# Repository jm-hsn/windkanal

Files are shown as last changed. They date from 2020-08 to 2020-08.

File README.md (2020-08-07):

# Windkanal HSN

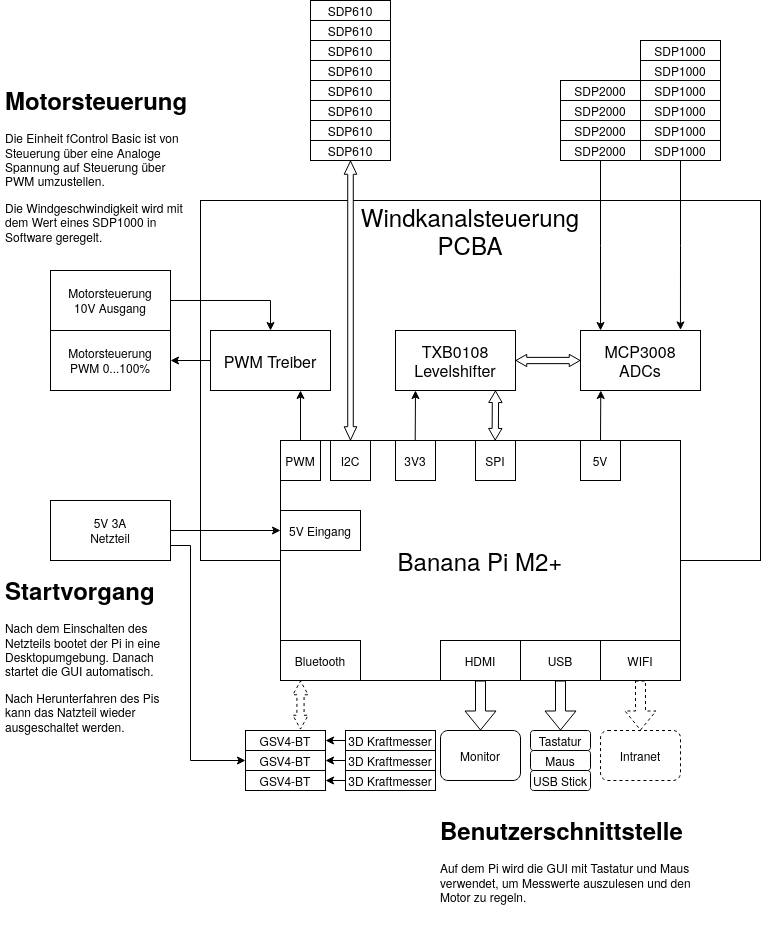
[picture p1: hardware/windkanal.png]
Hardware Chart


# Hardware
[PCB](https://easyeda.com/User201/windkanal)

[Gerber Dateien](hardware/pcb)

[Komponentenliste](hardware/bom.md)

## GPIO Pinout

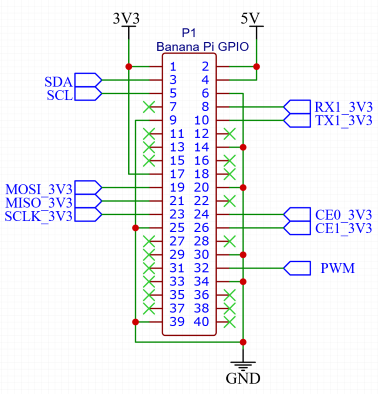
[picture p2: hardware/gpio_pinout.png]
GPIO Pinout


# Installation
[software/install.md](software/install.md)

# Starten

```bash
cd software/
python3 main.py
```

# Entwicklung
[software/ui/README.md](software/ui/README.md)

## Guides
PyQt5 Tutorial https://likegeeks.com/pyqt5-tutorial/

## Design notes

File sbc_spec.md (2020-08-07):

- bluetooth
  - serial over bt
  - bluetooth dongle?
- Raspberry Pi compatible GPIO
  - I2C
  - Parallel (bit-bang)

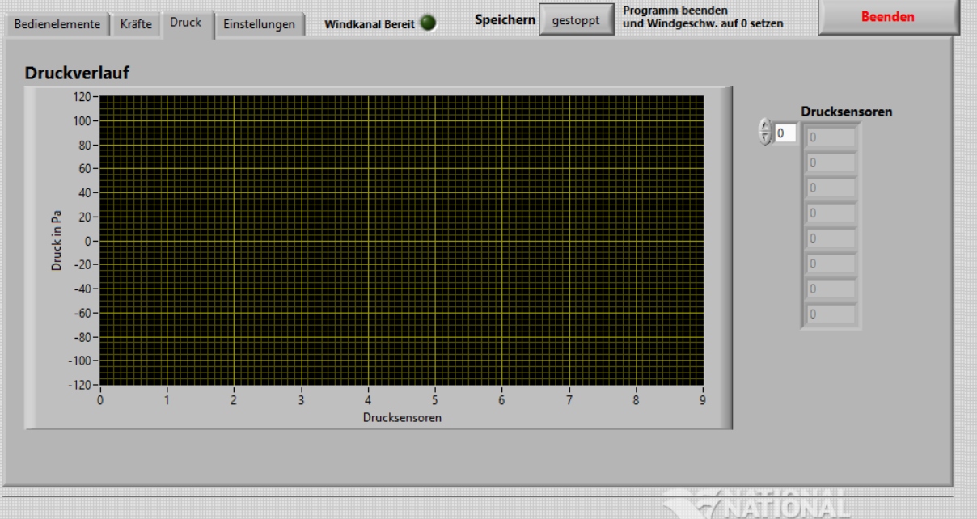
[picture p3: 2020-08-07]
software/labview/druck.jpg

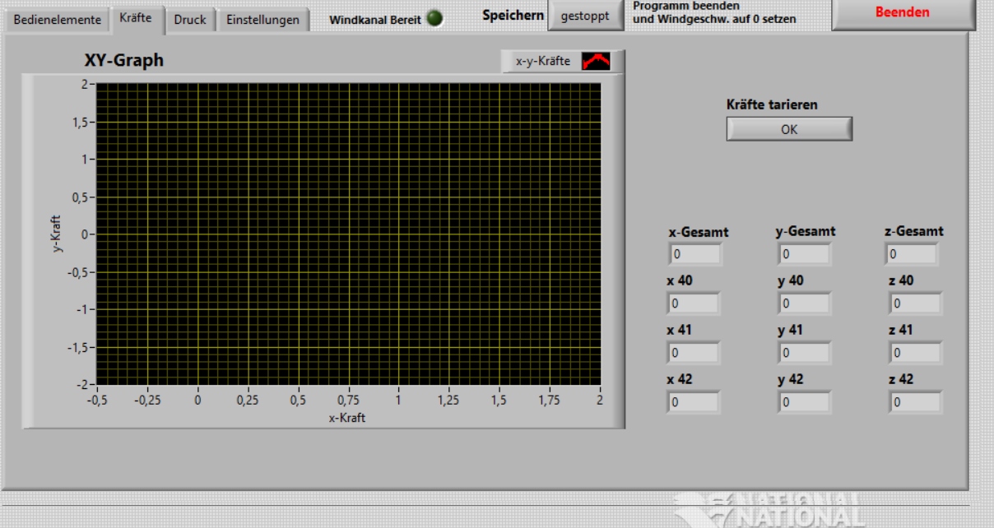
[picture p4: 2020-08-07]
software/labview/kräfte.jpg

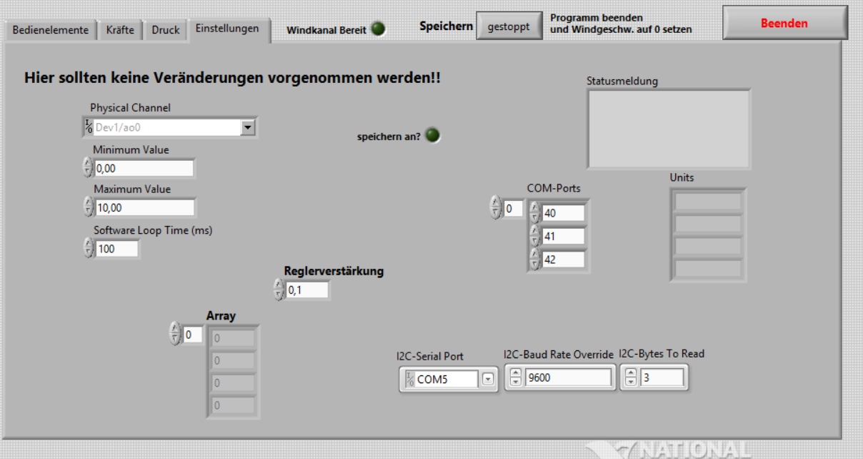
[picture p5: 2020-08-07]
software/labview/einstellungen.jpg

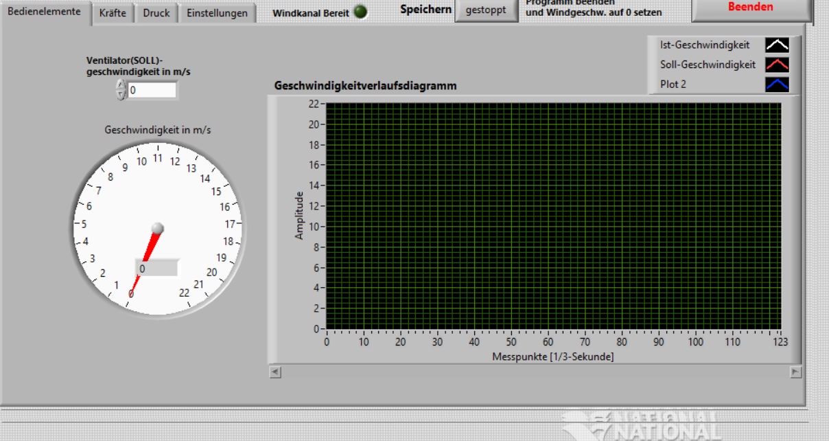
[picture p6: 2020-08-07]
software/labview/bedienelemente.jpg

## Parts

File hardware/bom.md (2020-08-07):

# Komponentenliste [BOM](hardware/pcb/bom.xlsx)

| Designator                                        | Name                         | Footprint    | Stück |
|---------------------------------------------------|------------------------------|--------------|-------|
| C1,C6,C2,C5                                       | SMD Kondensator              | 0805'        | 4     |
| R2,R3,R4,R5,R5,R7,R8                              | SMD Widerstand               | 0805'        | 7     |
| R1                                                | SMD Widerstand               | 0805'        | 1     |
| LED1                                              | Led Grün                     | 5mm          | 1     |
| LED2                                              | LED Rot                      | 5mm          | 1     |
| LED3                                              | LED Gelb                     | 5mm          | 1     |
| Q1,Q4                                             | SMD NPN Transistor           | SOT\-23      | 2     |
| Q2                                                | SMD PNP Transistor           | SOT\-23      | 1     |
| U2,U5                                             | 8\-Kanal SPI ADC             | SOIC\-16     | 2     |
| U4                                                | Bidirektionaler Pegelwandler | SSOP\-20     | 1     |
| JP1\-JP7                                          | Zweifach\-Schraubklemme      | 3,5mm pitch  | 15    |
| P1                                                | 2x20\-pin stackable Header   | 2,54mm pitch | 1     |
| H1                                                | 1x3\-pin stackable Header    | 2,54mm pitch | 1     |
| [PCB](https://easyeda.com/User201/windkanal) | 65mm x 65mm                  | \-           | 1     |
| Banana Pi BPI\-M2\+                               | Single\-Board\-Computer      | \-           | 1     |
| M2\.5 Abstandshalter für PI und PCB               | M2\.5, 10mm                  | \-           | 4     |
| Netzteil                                          | 5V 3A                        | \-           | 1     |
| HDMI Verlängerungskabel zum Einbau                | 1m                           | \-           | 1     |
| USB Verlängerungskabel zum Einbau                 | 0,5m                         | \-           | 2     |
| HDMI Kabel                                        | \-                           | \-           | 1     |
| HDMI Monitor                                      | \-                           | \-           | 1     |
| USB Hub                                           | \-                           | \-           | 1     |
| USB Tastatur                                      | \-                           | \-           | 1     |
| USB Maus                                          | \-                           | \-           | 1     |

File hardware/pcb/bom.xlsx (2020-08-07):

 | Windkanalsteuerung |  | Bill of Materials
 | Designator | Name | Footprint | Stück | Wert | Preis | Link | Preis 2 | Link 2 | Preis 2 | Link 3
Passiv
 | C1,C6,C2,C5 | SMD Kondensator | 0805' | 4 | 100n-10u | 1.12 € | https://www.mouser.de/ProductDetail/KEMET/C0805C105M8RACAUTO | (bulk) | Generischer SMD Kondensator |  | Lagerbestand?
 | R2,R3,R4,R5,R5,R7,R8 | SMD Widerstand | 0805' | 7 | 1k | 4.58 € | https://www.mouser.de/ProductDetail/KOA-Speer/RN73H2ATTD1001B25 | (bulk) | Generischer SMD Widerstand |  | Lagerbestand?
 | R1 | SMD Widerstand | 0805' | 1 | 270 Ohm | 0.12 € | https://www.mouser.de/ProductDetail/ROHM-Semiconductor/KTR10EZPJ271 | (bulk) | Generischer SMD Widerstand |  | Lagerbestand?
Aktiv
 | LED1 | Led Grün | 5mm | 1 |  | 0.23 € | https://www.mouser.de/ProductDetail/Kingbright/WP7113SGD | (bulk) | Generische LED |  | Lagerbestand?
 | LED2 | LED Rot | 5mm | 1 |  | 0.43 € | https://www.mouser.de/ProductDetail/Kingbright/WP57IID | (bulk) | Generische LED |  | Lagerbestand?
 | LED3 | LED Gelb | 5mm | 1 |  | 0.41 € | https://www.mouser.de/ProductDetail/Kingbright/WP57YYD | (bulk) | Generische LED |  | Lagerbestand?
 | Q1,Q4 | SMD NPN Transistor | SOT-23 | 2 | MMBT5551 | 0.32 € | https://www.mouser.de/ProductDetail/ON-Semiconductor/MMBT5551LT1G?qs=sGAEpiMZZMutXGli8Ay4kC402l06AIhPcyRrZFuJbVk%3D | (bulk) | Generischer SMD NPN Transistor |  | Lagerbestand?
 | Q2 | SMD PNP Transistor | SOT-23 | 1 | MMBT5401 | 0.15 € | https://www.mouser.de/ProductDetail/ON-Semiconductor/MMBT5401LT1G?qs=sGAEpiMZZMutXGli8Ay4kK2TqWlAzC1zwHYVH5ZeC0k%3D | (bulk) | Generischer SMD PNP Transistor |  | Lagerbestand?
ICs
 | U2,U5 | 8-Kanal SPI ADC | SOIC-16 | 2 | MCP3008-ISL | 3.94 € | https://www.mouser.de/ProductDetail/Microchip-Technology/MCP3008-I-SL?qs=sGAEpiMZZMvTvDTV69d2Qh8oAuXtCOKDL2vySlNGbrs%3D | 3.96 € | https://www.digikey.de/product-detail/de/microchip-technology/MCP3008-I%2FSL/MCP3008-I%2FSL-ND/319423 Acquisition&utm_source=google&utm_medium=cpc&utm_campaign=Google Shopping_Integrated Circuits (ICs)&utm_term=&productid=319423&gclid=EAIaIQobChMIiaT4psO65wIVCc93Ch1m9wqzEAkYASABEgIVtPD_BwE | 3.92 € | https://de.rs-online.com/web/p/a-d-wandler/7386651?s_kwcid=AL!8729!3!340765004536!!!g!339234251014!&matchtype=&pla-339234251014&gclsrc=aw.ds | .
 | U4 | Bidirektionaler Pegelwandler | SSOP-20 | 1 | TXB0108PW | 1.36 € | https://www.mouser.de/ProductDetail/Texas-Instruments/TXB0108PWR?qs=sGAEpiMZZMupTq4AYuRvQKKOVTxKvBsp | . |  | 1.49 € | https://de.rs-online.com/web/p/spannungswandler/7099038?s_kwcid=AL!8729!3!340765005052!!!g!341070930671!&matchtype=&pla-341070930671&gclsrc=aw.ds | .
Mechanisch
 | JP1-JP7 | Zweifach-Schraubklemme | 3,5mm pitch | 15 |  | 9.90 € | https://www.mouser.de/ProductDetail/Wurth-Elektronik/691214110002 | (bulk) | Generische reihbare Schraubklemme |  | Lagerbestand?
 | P1 | 2x20-pin stackable Header | 2,54mm pitch | 1 |  | 2.66 € | https://www.mouser.de/ProductDetail/SparkFun/PRT-12790 | (bulk) | auch normaler female Header mögl. |  | Lagerbestand?
 | H1 | 1x3-pin stackable Header | 2,54mm pitch | 1 |  | 0.47 € | https://www.mouser.de/ProductDetail/SparkFun/PRT-13875 | (bulk) | auch normaler female Header mögl. |  | Lagerbestand?
PCB
 | für die meisten Anbiebter als Gerber exportierbar |  | 65mm x 65mm | 1 |  | 5.00 € | https://easyeda.com/User201/windkanal | 25.99 € | https://aisler.net/p/VFZYHOGP | 53.61 € | https://aetzwerk.de/kalkulation | .
Sonstige
 | Banana Pi BPI-M2+ | Single-Board-Computer | - | 1 |  | 53.99 € | https://www.conrad.de/de/p/banana-pi-bpi-m2-1-gb-4-x-1-0-ghz-banana-pi-1435682.html | 39.99 € | https://www.pollin.de/p/banana-pi-m2-edu-entwicklungsboard-1gb-ddr3-810647 | 47.52 € | https://www.rakuten.de/produkt/sinovoip-banana-pi-bpi-m2h2-mini-quad-core-h2-single-board-computer-2424472665?cid=adwords | .
 | M2.5 Abstandshalter für PI und PCB |  | M2.5, 10mm | 4
 | Netzteil | 5V 3A | - | 1 |  |  |  |  |  |  | Lagerbestand?
 | HDMI Verlängerungskabel zum Einbau |  | 1m | 1 | (optional) | 11.99 € | https://www.conrad.de/de/p/hdmi-verlaengerungskabel-zum-einbau-1x-hdmi-stecker-1x-hdmi-buchse-1-m-schwarz-delock-1421657.html |  |  |  |  | .
 | USB Verlängerungskabel zum Einbau |  | 0,5m | 2 | (optional) | 16.98 € | https://www.conrad.de/de/p/delock-usb-2-0-anschlusskabel-1x-usb-2-0-stecker-a-1x-usb-2-0-buchse-a-0-5-m-schwarz-vergoldete-steckkontakte-1651192.html |  |  |  |  | .
 | HDMI Kabel |  | - | 1 |  |  |  |  |  |  | Lagerbestand?
 | HDMI Monitor |  | - | 1 |  |  |  |  |  |  | Lagerbestand?
 | USB Hub |  | - | 1 |  |  |  |  |  |  | Lagerbestand?
 | USB Tastatur |  | - | 1 |  |  |  |  |  |  | Lagerbestand?
 | USB Maus |  | - | 1 |  |  |  |  |  |  | Lagerbestand?
 |  |  |  |  |  | 113.65 €

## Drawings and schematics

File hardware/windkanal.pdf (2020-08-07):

# Windkanalsteuerung

# Motorsteuerung

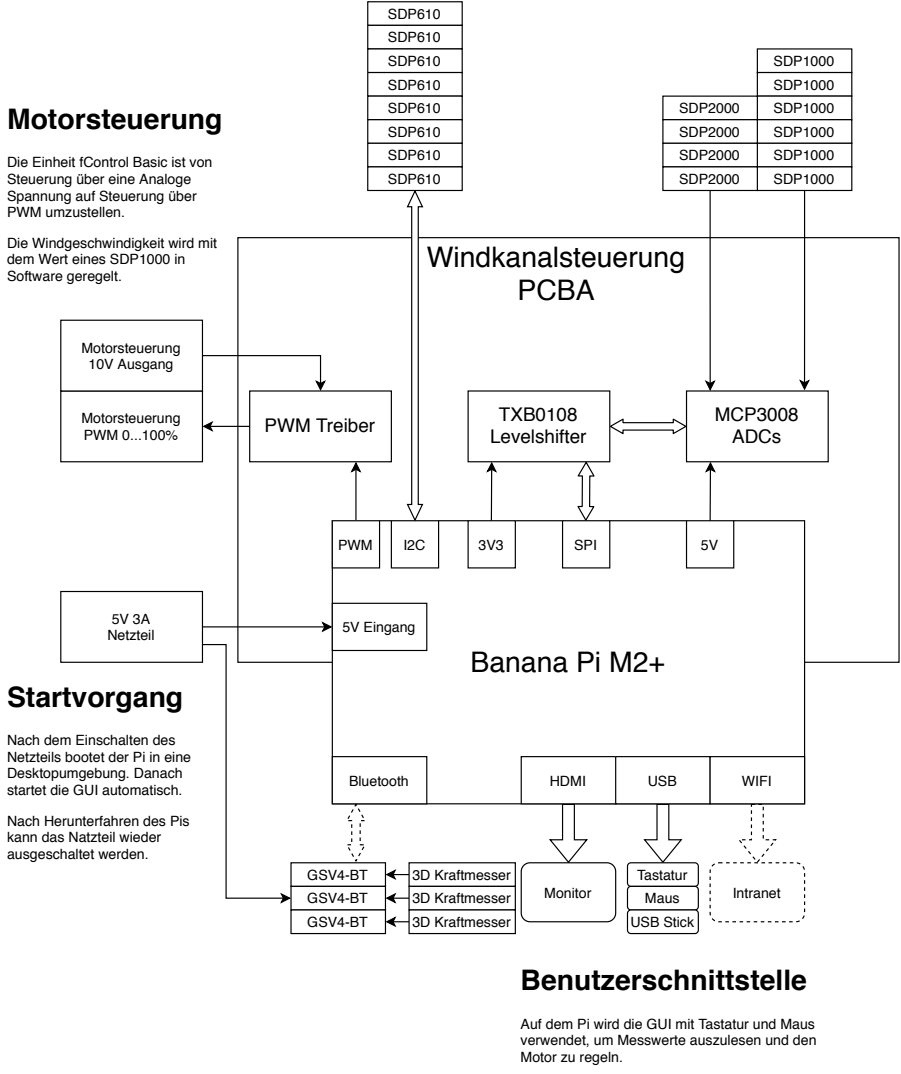
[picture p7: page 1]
Banana Pi M2+; SPI; Bluetooth; HDMI; USB; WIFI; PWM; PCBA; MCP3008 ADCs; 5V Eingang; SDP1000; SDP2000; TXB0108 Levelshifter; 5V 3A Netzteil; SDP610; Motorsteuerung 10V Ausgang; GSV4-BT; 3D Kraftmesser; Monitor; Tastatur; Maus; USB Stick; Intranet; Benutzerschnittstelle; Startvorgang

Die Einheit fControl Basic ist von
Steuerung über eine Analoge
Spannung auf Steuerung über
PWM umzustellen.

Die Windgeschwindigkeit wird mit
dem Wert eines SDP1000 in
Software geregelt.

PWM Treiber Motorsteuerung
PWM 0...100%

Nach dem Einschalten des
Netzteils bootet der Pi in eine
Desktopumgebung. Danach
startet die GUI automatisch.

Nach Herunterfahren des Pis
kann das Natzteil wieder
ausgeschaltet werden.

Auf dem Pi wird die GUI mit Tastatur und Maus
verwendet, um Messwerte auszulesen und den
Motor zu regeln.

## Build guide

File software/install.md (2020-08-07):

# Installation

# 1. Install System

Download image `Debian 9 with kernel 4.4.55_3` from http://wiki.banana-pi.org/Banana_Pi_BPI-M2%2B#Raspbian

Write image to SD card
``` bash
sudo fdisk -l
# SD card is /dev/mmcblk1

unzip 2018-11-09-debian-9-stretch-mate-desktop-preview-bpi-m2p-4.4-sd-emmc.img.zip

sudo dd if=2018-11-09-debian-9-stretch-mate-desktop-preview-bpi-m2p-sd-emmc.img of=/dev/mmcblk1 bs=10MB
```
Boot Banana Pi from SD card

# 2. Bluetooth Setup

``` bash
sudo apt update
sudo apt upgrade -y
sudo apt install libdbus-1-dev libglib2.0-dev libudev-dev libical-dev libreadline-dev

wget http://www.kernel.org/pub/linux/bluetooth/bluez-5.49.tar.xz

tar -xf bluez-5.49.tar.xz && rm bluez-5.49.tar.xz

cd bluez-5.49/

./configure --prefix=/usr --mandir=/usr/share/man --sysconfdir=/etc --localstatedir=/var --enable-experimental

make -j4

sudo make install

sudo adduser pi bluetooth
```

# 3. Edit bluetooth.conf
Add the marked lines to `bluetooth.conf`

```bash 
sudo cp /etc/dbus-1/system.d/bluetooth.conf /etc/dbus-1/system.d/bluetooth.conf.bak
sudo nano /etc/dbus-1/system.d/bluetooth.conf
```

```xml
<policy user="root">
    <allow own="org.bluez"/>
    <allow send_destination="org.bluez"/>
    <allow send_interface="org.bluez.Agent1"/>
    <allow send_interface="org.bluez.MediaEndpoint1"/>
    <allow send_interface="org.bluez.MediaPlayer1"/>
    <allow send_interface="org.bluez.Profile1"/>
    <!-- add start -->
        <allow send_interface="org.bluez.AlertAgent1"/>
        <allow send_interface="org.bluez.ThermometerWatcher1"/>
        <allow send_interface="org.bluez.HeartRateWatcher1"/>
        <allow send_interface="org.bluez.CyclingSpeedWatcher1"/>
    <!-- add end -->
    <allow send_interface="org.bluez.GattCharacteristic1"/>
    <allow send_interface="org.bluez.GattDescriptor1"/>
    <allow send_interface="org.bluez.LEAdvertisement1"/>
    <allow send_interface="org.freedesktop.DBus.ObjectManager"/>
    <allow send_interface="org.freedesktop.DBus.Properties"/>
  </policy>

  <!-- add start -->
    <!-- allow users of bluetooth group to communicate -->
    <policy group="bluetooth">
        <allow send_destination="org.bluez"/>
    </policy>
  <!-- add end -->

  <policy at_console="true">
    <allow send_destination="org.bluez"/>
  </policy>
```
# 4. Reboot
```bash
sudo reboot
```
# 5. Test Bluetooth

```bash
$ rfkill list

    0: sunxi-bt: Bluetooth
        Soft blocked: no
        Hard blocked: no
    1: phy0: Wireless LAN
        Soft blocked: yes
        Hard blocked: no
    2: brcmfmac-wifi: Wireless LAN
        Soft blocked: yes
        Hard blocked: no
    4: hci0: Bluetooth
        Soft blocked: yes <--
        Hard blocked: no

$ rfkill unblock bluetooth

    0: sunxi-bt: Bluetooth
        Soft blocked: no
        Hard blocked: no
    1: phy0: Wireless LAN
        Soft blocked: yes
        Hard blocked: no
    2: brcmfmac-wifi: Wireless LAN
        Soft blocked: yes
        Hard blocked: no
    4: hci0: Bluetooth
        Soft blocked: no <--
        Hard blocked: no
```
Try pairing a device
```bash
$ bluetoothctl

> power on

> agent on

> scan on

# wait a few seconds

> scan off

> pair 00:0B:CE:04:F6:66

    Attempting to pair with 00:0B:CE:04:F6:66
    Request PIN code
    [blue1m[agent] Enter PIN code: 0000

    [CHG] Device 00:0B:CE:04:F6:66 Connected: yes
    [CHG] Device 00:0B:CE:04:F6:66 UUIDs: 00001101-0000-1000-8000-00805f9b34fb
    [CHG] Device 00:0B:CE:04:F6:66 ServicesResolved: yes
    [CHG] Device 00:0B:CE:04:F6:66 Paired: yes
    Pairing successful

> info 00:0B:CE:04:F6:66

    Device 00:0B:CE:04:F6:66 (public)
    	Name: BAmobile
    	Alias: BAmobile
    	Class: 0x00001f00
    	Paired: yes
    	Trusted: no
    	Blocked: no
    	Connected: no
    	LegacyPairing: yes
    	UUID: Serial Port               (00001101-0000-1000-8000-00805f9b34fb)

> quit
```
Try to send a packet
```bash
sudo rfcomm bind 0 00:0B:CE:04:F6:66

sudo rfcomm show /dev/rfcomm0 0
#rfcomm0: 00:0B:CE:04:F6:66 channel 1 clean

#test send
sudo python3 -c 'print("\26\01\62\65\72\6c\69\6e")' > /dev/rfcomm

#test receive
cat /dev/rfcomm0
```
# 6. Install python
```bash
sudo apt update
sudo apt upgrade -y
sudo apt autoremove

sudo apt install python3-dev python3-pip python3-matplotlib

python3 -m pip install -U pip setuptools
python3 -m pip install -U matplotlib
```

## 6.1 Install pybluez for python
```bash
sudo apt-get install bluez bluez-tools
sudo apt install libbluetooth-dev

python3 -m pip install wheel pybluez
```

## 6.2 Install tkinter frontend
``` bash
sudo apt install python3-tk
python3 -m pip install tk-tools
```

## 6.3 Install SPI support
Install https://github.com/doceme/py-spidev

``` bash
python3 -m pip install spidev
```

Warning: Doesn't work on `Debian 9 with kernel 4.4.55_3`

Workaround: use gpio bitbang instead of spi device

## 6.4 Install I2C support
```bash
sudo apt install python3-smbus
python3 -m pip install smbus
```

# 7. Fix `bluetoothd` service
Edit `dbus-org.bluez.service`
```bash
sudo nano /etc/systemd/system/dbus-org.bluez.service
```
change
> ExecStart=/usr/lib/bluetooth/bluetoothd

into
> ExecStart=/usr/lib/bluetooth/bluetoothd -C

```bash
sudo systemctl daemon-reload
sudo sdptool add SP
```

# 8. Run Python serial examples

```bash
python3 tests/btSend.py

sudo hciconfig hci0 piscan

python3 tests/btRecv.py
```

# 9. Build and run Frontend

```bash
./run.sh
```

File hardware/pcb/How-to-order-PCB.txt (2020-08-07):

How to Order PCB

Please refer to:
https://docs.easyeda.com/en/PCB/Order-PCB

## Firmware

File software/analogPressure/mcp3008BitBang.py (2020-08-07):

#!/usr/bin/env python
#
# Bitbang'd SPI interface with an MCP3008 ADC device
# MCP3008 is 8-channel 10-bit analog to digital converter
#  Connections are:
#     CLK => 18  
#     DOUT => 23 (chip's data out, RPi's MISO)
#     DIN => 24  (chip's data in, RPi's MOSI)
#     CS => 25 

import RPi.GPIO as GPIO
import time
import sys

CLK = 23
MISO = 21
MOSI = 19
CS0 = 24
CS1 = 26

def setupSpiPins(clkPin, misoPin, mosiPin, csPin):
    ''' Set all pins as an output except MISO (Master Input, Slave Output)'''
    GPIO.setup(clkPin, GPIO.OUT)
    GPIO.setup(misoPin, GPIO.IN)
    GPIO.setup(mosiPin, GPIO.OUT)
    GPIO.setup(csPin, GPIO.OUT)
     

def readAdc(channel, clkPin, misoPin, mosiPin, csPin):
    if (channel < 0) or (channel > 7):
        print("Invalid ADC Channel number, must be between [0,7]")
        return -1
        
    # Datasheet says chip select must be pulled high between conversions
    GPIO.output(csPin, GPIO.HIGH)
    
    # Start the read with both clock and chip select low
    GPIO.output(csPin, GPIO.LOW)
    GPIO.output(clkPin, GPIO.HIGH)
    
    # read command is:
    # start bit = 1
    # single-ended comparison = 1 (vs. pseudo-differential)
    # channel num bit 2
    # channel num bit 1
    # channel num bit 0 (LSB)
    read_command = 0x18
    read_command |= channel
    
    sendBits(read_command, 5, clkPin, mosiPin)
    
    adcValue = recvBits(12, clkPin, misoPin)
    
    # Set chip select high to end the read
    GPIO.output(csPin, GPIO.HIGH)
  
    return adcValue
    
def sendBits(data, numBits, clkPin, mosiPin):
    ''' Sends 1 Byte or less of data'''
    
    data <<= (8 - numBits)
    
    for bit in range(numBits):
        # Set RPi's output bit high or low depending on highest bit of data field
        if data & 0x80:
            GPIO.output(mosiPin, GPIO.HIGH)
        else:
            GPIO.output(mosiPin, GPIO.LOW)
        
        # Advance data to the next bit
        data <<= 1
        
        # Pulse the clock pin HIGH then immediately low
        GPIO.output(clkPin, GPIO.HIGH)
        GPIO.output(clkPin, GPIO.LOW)

def recvBits(numBits, clkPin, misoPin):
    '''Receives arbitrary number of bits'''
    retVal = 0
    
    for bit in range(numBits):
        # Pulse clock pin 
        GPIO.output(clkPin, GPIO.HIGH)
        GPIO.output(clkPin, GPIO.LOW)
        
        # Read 1 data bit in
        if GPIO.input(misoPin):
            retVal |= 0x1
        
        # Advance input to next bit
        retVal <<= 1
    
    # Divide by two to drop the NULL bit
    return (retVal/2)
    
    
if __name__ == '__main__':
    try:
        GPIO.setmode(GPIO.BOARD)
        setupSpiPins(CLK, MISO, MOSI, CS0)
    
        while True:
            val = readAdc(0, CLK, MISO, MOSI, CS0)
            print("ADC Result: ", str(val))
            time.sleep(.3)
    except KeyboardInterrupt:
        GPIO.cleanup()
        sys.exit(0)
